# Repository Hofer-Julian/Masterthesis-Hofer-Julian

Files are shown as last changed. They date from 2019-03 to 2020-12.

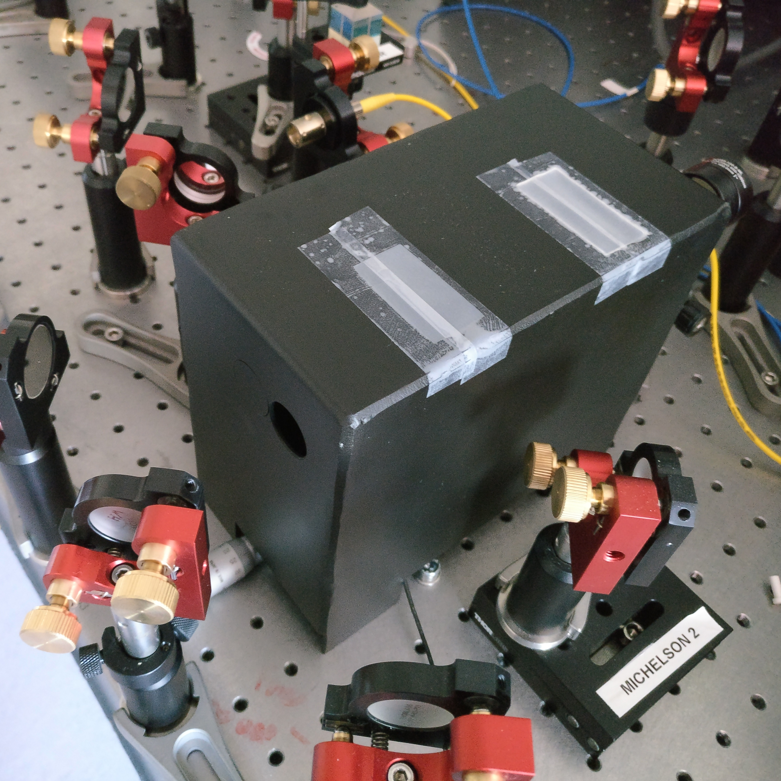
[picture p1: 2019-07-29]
figures/fabry-perot/setup/casing.jpg

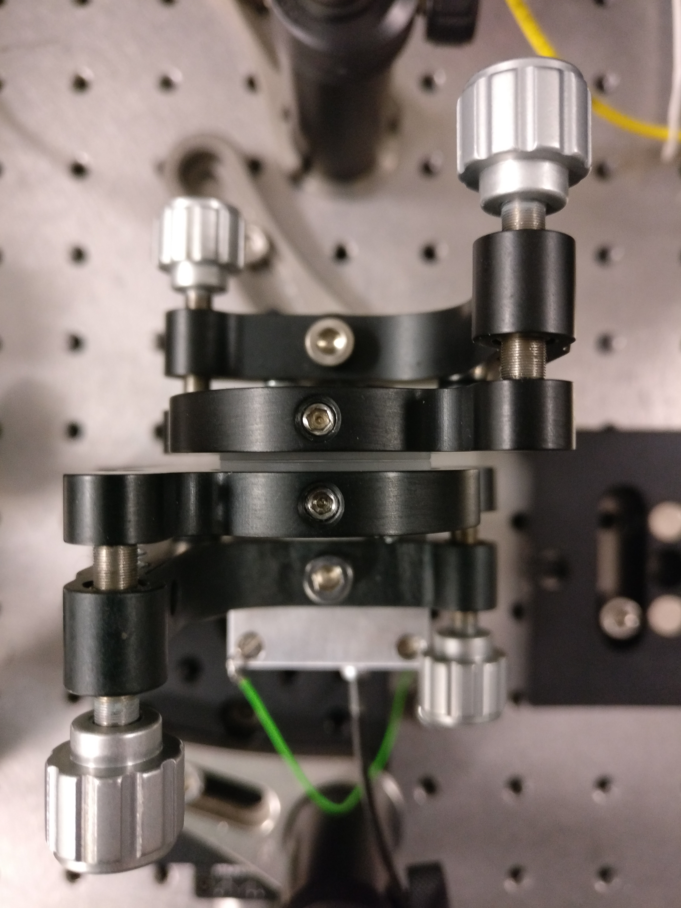
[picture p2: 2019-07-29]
figures/fabry-perot/setup/processing/topview.jpg

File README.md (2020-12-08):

# Advanced excitation and spectroscopy schemes of single quantum dots 

In this thesis excitation of quantum dots via adiabatic rapid passage and spectroscopy of quantum dot emission with a scanning Fabry Pérot interferometer (FPI) are discussed.

First, the use of GaAs quantum dots as sources of (entangled) single photons is motivated and details of their fabrication and optical properties are presented.
The optical setup used for the measurements is sketched and methods like micro photo-luminescence are explained.
Subsequently, the use of adiabatic rapid passage for entangled photon generation is motivated and its implementation with frequency-chirped pulses is explained.

The theory behind the chirp is presented, leading to the description of a setup used to deterministically adjust the chirp of a laser beam.
The chirped beam was measured with an interferometric autocorrelator and the numerical filter MOSAIC was used to extract the chirp parameter from these measurements.

Also, scanning FPIs as tools to resolve fine features of quantum dot emission are presented.
The reader is guided through the theory of Gaussian beams and the calculation of common FPI properties, ranging from resonator losses to its transmission spectrum.
Methods to suppress higher Gauss modes are presented and simulations are shown used to size the FPI.
Finally, measurements with fast photodiodes and CCD sensors are presented and with them the suitability for resolving the fine structure of a GaAs quantum dot is shown.   

------------------
<sub>Masterthesis, 10/2019, Johannes Kepler University, Linz/Austria<sub>

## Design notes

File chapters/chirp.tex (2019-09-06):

% !TEX root = ../masterthesis.tex
\chapter{Entangled photon generation using adiabatic rapid passage with frequency-chirped pulses}
\label{cha:chirp}

\section{Introduction and motivation}

In order to efficiently use the biexciton decay cascade, the \acl{XX} state has to be prepared beforehand in a robust way.
This chapter deals with the efficient inversion of the \ac{QD} from the ground state to the biexciton level via \ac{ARP}.
\acs{ARP} uses chirped pulses, which need to be measured and deterministically adjusted in order to effectively use them.
Therefore, the majority of this chapter will focus on the chirp and how to determine and adjust it, with the help of simulations and later with measurements.

\section{Chirp}
\label{sec:chirp}
A chirped signal is a signal whose frequency changes over time.
For example, the frequency of a linearly chirped signal $f(t)$ would be described by
\begin{equation}
f(t) = ct+f_0
\end{equation}
where $f_0$ is the starting frequency at $t=0$ and $c$ is the chirpyness. A linearly chirped sinusoidal wave is depicted in figure~\ref{fig:chirped-sin}.

\begin{figure}[H]
	\centering
	
	\caption{A chirped sinusoidal wave which increases in frequency over time.}
	\label{fig:chirped-sin}
\end{figure}

As this chapter is concentrated on exciting \acp{QD} with frequency-chirped pulses, the mathematical description of chirped laser pulses will now be discussed. The shape of the electric field of a laser $E(t)$ can be approximated by
\begin{equation}
\label{eq:electric-field-laser}
E(t) \sim \mathrm{Re}\left(f^{1/2}(t) \cdot \exp\left(-i \omega t - i \phi(t)\right)\right)
\end{equation}
with the central frequency $\omega$ and the linear chirp $\phi(t)$.

Depending on the laser either a Gaussian or a hyperbolic secant describes the pulse shape more accurately~\cite{glassl_biexciton_2013, hirayama_real-time_2002}

\begin{itemize}
	\item Gaussian pulse:
	\begin{itemize}
		\item Pulse shape of
		\begin{equation}
		\label{eq:f_gauss}
		f_{gauss}(t) = \left(\frac{A_{gauss}}{\sqrt{2 \cdot \pi \cdot \tau_0 \cdot \tau}} \exp\left(-\frac{t^2}{2 \cdot \tau^2}\right)\right)^2
		\end{equation}
		with the normalization constant $A_{gauss}$, the pulse duration $\tau_0$, the central frequency $\omega$ and the chirp coefficient $\alpha$.
		\item Linear chirp of
		\begin{equation}
		\label{eq:phi-gauss}
		\phi_{gauss}(t) = \frac{a_{gauss} t^2}{2}
		\end{equation}
		where 
		\begin{equation}
		\tau = \sqrt{\alpha^2 / \tau_0^2 + \tau_0^2}
		\end{equation}
		characterizes the chirped pulse length and
		\begin{equation}
		\label{eq:chirp-parameter}
		a = \alpha / (\alpha ^ 2 + \tau _0 ^ 4)
		\end{equation}
		is the frequency chirp rate.
	\end{itemize}
	\newpage
	\item Secant pulse:
	\begin{itemize}
		\item Pulse shape of
		\begin{equation}
		f_{secant}(t) = A_{secant} \cdot \textrm{sech}^2\left(\frac{t}{\tau_0}\right) = A_{secant} \cdot \left(\frac{2}{\exp(\frac{t}{\tau_0}) + \exp(-\frac{t}{\tau_0})}\right)^2
		\end{equation}
		with the normalization constant $A_{secant}$, the pulse duration $\tau_0$, the central frequency $\omega$ and the chirp coefficient $\alpha$.
		\item Linear chirp of
		\begin{equation}
		\phi_{secant}(t) = \alpha_{secant}\left(\frac{t}{\tau_0}\right)^2
		\end{equation}
	\end{itemize}
\end{itemize}

The following discussion will assume a Gaussian laser shape as described by equation~\eqref{eq:f_gauss} and \eqref{eq:phi-gauss}.
A simulation for $E$ is plotted in figure~\ref{fig:chirpedlaserpulse} for different chirp parameters $\alpha$ suitable to display examples for strong and weak chirps.
As can be seen there, the chirp parameter strongly influences the shape of the electric field.
If $E$ could be measured directly, the chirp could be easily estimated.
This is not feasible in our case, as our Ti:Sa laser can produce laser pulses as short as \SI{100}{\femto \second} and response times of photodiodes and oscilloscopes are in the best case in the order of \SI{200}{\femto \second}.
This means they cannot even measure the duration of these ultrashort pulses let alone resolve the pulse shape.

\begin{figure}[H]
	\centering
	
	\caption{Electric field $E$ of Gaussian laser pulse of pulse duration $\tau_0=\SI{0.5}{\pico \second}$ for chirp of (a) $\alpha = \SI{0.1}{\pico \second \squared}$ and (b) $\alpha = \SI{0.5}{\pico \second \squared}$}
	\label{fig:chirpedlaserpulse}
\end{figure}

\newpage

\section{Measuring the chirp with interferometric autocorrelation}
\begin{figure}[H]
	\centering
	
	\caption[Schematics of an interferometric autocorrelator]{Schematics of an interferometric autocorrelator, where \textbf{L} is a converging lens, \textbf{SHG} a second-harmonic generation crystal, \textbf{BS} a beam splitter, \bm{$\tau$} the interval between two pulses, \textbf{D} the detector and \textbf{F} a spectral filter to block the fundamental wavelength~\cite{noauthor_optical_nodate}.}
	\label{fig:optical-field-autocorrelation-setup}
\end{figure}
In order to estimate the pulse width $\tau_0$, \ac{IAC} is used.
Basically, a nonlinear crystal is added to a Michelson interferometer in order to generate a signal governed by
\begin{equation}
\label{eq:i-m-integral}
I_M(\tau) = \int_{-\infty}^{+\infty}\langle|(E(t)+E(t-\tau))^2|^2\rangle dt.
\end{equation}
and plotted in figure~\ref{fig:imgausschirpwithoutslitwithoutmosaic}~\cite{diels_ultrashort_2006}.
Here, $\langle \rangle$ denotes averaging over fast oscillations of the electric field.
\begin{figure}[H]
	\centering
	
	\caption{Intensity of IAC of a Gaussian laser pulse of pulse duration $\tau_0=\SI{0.5}{\pico \second}$ without applied MOSAIC filter for chirp of (a) $\alpha = \SI{0.1}{\pico \second \squared}$ and (b) $\alpha = \SI{0.5}{\pico \second \squared}$}
	\label{fig:imgausschirpwithoutslitwithoutmosaic}
\end{figure}
Under the use of equation~\ref{eq:electric-field-laser}, equation~\eqref{eq:i-m-integral} can be expanded to
\begin{align}
I(\tau) = 1 &+ 2 \int f(t) f(t + \tau) dt + \int f(t) f(t + \tau) \cos(2 \omega \tau + 2 \Delta \phi) dt \nonumber\\
&+ 2 \int f^{1/2}(t) f^{3/2}(t + \tau) \cos(\omega \tau + \Delta \phi) dt + 2 \int f^{3/2}(t) f^{2/2}(t + \tau) \cos(\omega \tau + \Delta \phi) dt
\end{align}
where $\Delta \phi(t, \tau) = \phi(t + \tau) - \phi(t)$ and $\int f(t) dt = 1$.

As can be seen in figure~\ref{fig:imgausschirpwithoutslitwithoutmosaic}, the chirp parameter $\alpha$ has hardly any measurable influence on the resulting signal.
However, certain modifications to the \ac{IAC} signal introduced by \textcite{hirayama_real-time_2002} make it much more sensitive to the temporal chirp.
It is called \ac{MOSAIC} and performs the following transformations on the \ac{IAC} spectrum: The $\omega$ terms are eliminated and the $2\omega$ term is doubled.
The \ac{MOSAIC} signal is then described by
\begin{equation}
\label{eq:i-m-filtered}
I_{M}(\tau) = 1 + 2 \int f(t) f(t + \tau) dt + 2 \int f(t) f(t + \tau) \cos(2\omega \tau + 2\Delta \phi) dt.
\end{equation}
When the MOSAIC filter is applied to the data in figure~\ref{fig:imgausschirpwithoutslitwithoutmosaic}, this results in a signal as shown in figure~\ref{fig:mosaicchirpedlaserpulse}.
Here the influence of the chirp is clearly visible in the lower envelope.
\begin{figure}[H]
	\centering
	
	\caption{Intensity of IAC of a Gaussian laser pulse of pulse duration $\tau_0=\SI{0.5}{\pico \second}$ for chirp of (a) $\alpha = \SI{0.1}{\pico \second \squared}$ and (b) $\alpha = \SI{0.5}{\pico \second \squared}$}
	\label{fig:mosaicchirpedlaserpulse}
\end{figure}

\newpage

The points of the lower envelope can be obtained by determining the local minima of the signal as shown in figure~\ref{fig:mosaicchirpedlaserpulsefindenvelope}.

\begin{figure}[H]
	\centering
	
	\caption{Intensity of IAC of a Gaussian laser pulse of pulse duration $\tau_0=\SI{0.5}{\pico \second}$ with applied MOSAIC filter for chirp of (a) $\alpha = \SI{0.1}{\pico \second \squared}$ and (b) $\alpha = \SI{0.5}{\pico \second \squared}$.
		The orange dots are results of a numerical peak finder algorithm, executed in order to find local minima.}
	\label{fig:mosaicchirpedlaserpulsefindenvelope}
\end{figure}

The lower bound (minima envelope) of the MOSAIC trace can be derived by use of a standard textbook procedure~\cite{klein_optics_1986}
\begin{equation}
S^{min}_{MOSAIC}(\tau)= 1 + 2 \cdot g(\tau) - 2 \cdot [g_s^2(\tau)+g_c^2(\tau)]^{1/2}
\end{equation}
with
\begin{align}
g(\tau)&=\int f(t)f(t+\tau)dt\\
g_s(\tau)&=\int f(t)f(t+\tau)\sin(2\Delta\phi)dt\\
g_c(\tau)&=\int f(t)f(t+\tau)\cos(2\Delta\phi)dt.
\end{align}
The points of the lower envelope determined before can now be fitted in order to obtain the chirp parameter $\alpha$ as shown in figure~\ref{fig:mosaicchirpedlaserpulsefitenvelope}.
It is visible that the fitted values of $\alpha$ correspond to the expected values.
\begin{figure}[H]
	\centering
	
	\caption[Intensity of IAC of a Gaussian laser pulse of pulse duration $\tau_0=\SI{0.5}{\pico \second}$ with applied MOSAIC filter and fitted $\alpha$-values.]{Intensity of IAC of a Gaussian laser pulse of pulse duration $\tau_0=\SI{0.5}{\pico \second}$ with applied MOSAIC filter for chirp of (a) $\alpha = \SI{0.1}{\pico \second \squared}$ and (b) $\alpha = \SI{0.5}{\pico \second \squared}$.
		The orange line is a fit for the lower envelope of the MOSAIC signal in order to obtain~$\alpha$.}
	\label{fig:mosaicchirpedlaserpulsefitenvelope}
\end{figure}

\section{Deterministically adjusting the chirp with a pulse expander}
\label{sec:pulse-expander}
\begin{figure}[H]
	\centering
	
	\caption[Scheme of a folded pulse expander as described by \textcite{martinez_3000_1987}.]{Scheme of a folded pulse expander as described by \textcite{martinez_3000_1987}.
		The light enters on the right side, passes the halfmirror, and enters the system of transmission grating, lens and mirrors.
		Afterwards it hits the halfmirror and exits on the left hand.
		It induces an accumulated group velocity dispersion on the signal depending on the optical distance between the transmission grating and the lens.}
	\label{fig:pulse-expander}
\end{figure}

In the optimal case the chirp of the pulse can be deterministically adjusted in order to most efficiently excite the \ac{QD} via adiabatic rapid passage (going to be introduced in section~\ref{sec:arp}).
Grating compressors as discussed by \textcite{martinez_3000_1987} were originally used to compensate the broadening effect fibers have on pulses.
However, together with a telescope they have the inverse effect and can be used to induce a chirp.
A setup like this is sketched in figure~\ref{fig:pulse-expander} and it will in future references in this work be called \textit{pulse expander}.
Its main elements are a transmission grating and a lens.
This folded setup uses a mirror after the lens so that only one lens and one mirror are needed.
The accumulated group velocity dispersion $\frac{d^2 \Phi}{d \omega^2}$ can be adjusted by varying the optical distance $d$ between the focal plane of the lens and the transmission grating and is described by
\begin{equation}
\frac{d^2 \Phi}{d \omega^2} = k \beta^2 2 d
\end{equation}
where $k$ is the wavenumber and $\beta$ is given by
\begin{equation}
\beta = \frac{\lambda}{2 \pi w_0 \cos \theta}
\end{equation}
with $\lambda$ denoting the centre wavelength, $w_0$ the beam waist (beam size at the point of its focus) and $\theta$ the emerging angle as sketched in figure~\ref{fig:pulse-expander}.

\begin{figure}[H]
	\centering
	
	\caption{Influence of group velocity dispersion for example inside a fiber on a Gaussian pulse~\cite{orfanidis_electromagnetic_2002}}
	\label{fig:group-velocity-dispersion}
\end{figure}

As can be seen in figure~\ref{fig:group-velocity-dispersion}, a group velocity dispersion has a similar effect on a Gaussian pulse as a chirp.
In fact, the frequency chirp rate $a_{gauss}$ introduced in equation~\eqref{eq:phi-gauss} can be put into relation with it by:~\cite{orfanidis_electromagnetic_2002}
\begin{equation}
a_{gauss} = \frac{\frac{d^2 \Phi}{d \omega^2}}{\tau_0^4 + \left(\frac{d^2 \Phi}{d \omega^2}\right)^2}
\end{equation}

\section{Adiabatic rapid passage}
\label{sec:arp}
One way to invert the \ac{QD} from the ground state $\ket{G}$ to the biexciton state $\ket{XX}$ is by exciting it with a narrow-band laser pulse of constant centre frequency, which equals to half of the ground state biexciton transition frequency.
As described in equation~\eqref{eq:n-xx}, if the pulse area $\theta=\pi$, a population inversion from the $\ket{G}$ state to the $\ket{XX}$ occurs.
However, the $\pi$-pulse method is not a generally robust scheme.
In order to ensure the inversion, precise control of the field intensity is required~\cite{glassl_biexciton_2013}.
Adiabatic rapid passage \acused{ARP} (\acs{ARP}) with frequency chirped pulses is a much more robust alternative to this Rabi-flopping scheme.
Here, the frequency of the laser signal is swept through resonance, starting slightly above or below the resonance frequency.
The biexciton state can be populated with nearly perfect efficiency~\cite{glassl_biexciton_2013} if the process is performed adiabatically, i.e. if~\cite{malinovsky_general_2001}
\begin{equation}
\Omega_0^2 \gg |\frac{d}{dt} \omega(t)|
\end{equation}
where $\Omega_0$ is the peak Rabi frequency and $\omega(t)$ is the center frequency of the laser pulse. 

In figure~\ref{fig:biexciton-occupation} simulations in order to determine the final biexciton occupation for different biexciton binding energies $\Delta$ by \textcite{glassl_biexciton_2013} are presented.
Here, a linearly-chirped Gaussian laser pulse as discussed in section~\ref{sec:chirp} was assumed.
\begin{figure}[H]
	\centering
	
	\caption[Final biexciton occupation after chirped Gaussian pulse of pulse duration $\tau_0 = \SI{2}{\pico \second}$]{Final biexciton occupation after chirped Gaussian pulse of pulse duration $\tau_0 = \SI{2}{\pico \second}$.
		It is plotted against the original pulse area $A$ (vertical axis) and the chirp parameter $\alpha$ for biexciton binding energies of (a) $\Delta=0$, (b) 1, and (c) \SI{3}{\milli \electronvolt}~\cite{glassl_biexciton_2013}.}
	\label{fig:biexciton-occupation}
\end{figure}
The central frequency is chosen so that for $\alpha=0$ it resonates to groundstate-to-biexction transition, which is sketched in figure~\ref{fig:biexciton-occupation}.
For $\alpha=0$ Rabi oscillations are visible and their period depends strongly on the biexciton binding energy $\Delta$.
However, for $\alpha \gg 0$ biexciton preparation becomes insensitive to small variations of the pulse area $A$ as long it exceeds a certain threshold.
This is therefore the regime which would be the most suitable to work in.
In the case of $\alpha < 0$ this insensitivity does not appear for moderate values of $\Delta$ as can be seen in figure~\ref{fig:biexciton-occupation}(b).

\newpage
\section{Measurements and discussion}
As discussed in the sections above, the final goal is to excite a \ac{QD} via \ac{ARP}.
The first step to do that is to determine the chirp of a laser pulse which only passed the pulse shaper with the \ac{IAC}.
Here a laser pulse of only $\tau_0=\SI{344}{\femto \second}$ was used as the \ac{IAC} can not resolve fine enough details for greater $\tau_0$.
Even though broader peaks will be necessary in order to excite the \ac{QD} with \ac{ARP}, this is not a problem as the equivalent chirp can be calculated for greater $\tau_0$ with equation~\eqref{eq:chirp-parameter}.

Afterwards, a signal was measured after passing a pulse expander as discussed in section~\ref{sec:pulse-expander} and sketched in figure~\ref{fig:setupflat}.
The comparison between these two is shown in figure~\ref{fig:measuredchirpedlaserpulsebeforemosaic}.
Compared to the simulations in figure~\ref{fig:imgausschirpwithoutslitwithoutmosaic} it is visible that the \ac{IAC} of the laser pulse without the pulse expander fits the expected shape well, while the one with the pulse expander does not.
Possible reasons could be that the chirp is too high for the model used in the simulation to work or that the pulse expander introduces side effects not considered in the simulation.

\begin{figure}[H]
	\centering
	
	\caption{Measured IAC of Ti:Sa Laser without (a) and with (b) pulse expander before the autocorrelator.}
	\label{fig:measuredchirpedlaserpulsebeforemosaic}
\end{figure}

The same signals after applying the \ac{MOSAIC} filter are shown in figure~\ref{fig:measuredchirpedlaserpulseaftermosaic}.
It is visible that the lower envelopes in figure~\ref{fig:measuredchirpedlaserpulseaftermosaic}a and \ref{fig:measuredchirpedlaserpulseaftermosaic}b do not resemble the expected ones in figure~\ref{fig:mosaicchirpedlaserpulse}.
As the laser signal without pulse expander was assumed to be relatively unchirped, it is already unexpected that the lower envelope differs that much from a constant line at zero intensity.
One explanatory approach could be that the laser was already chirped to begin with. However, this would not explain why the shape of the lower envelope differs from the characteristic one of the simulation.
The next approach was to send the laser without pulse shaper into the \ac{IAC}.
However, the envelope of the signal after applying the \ac{MOSAIC} filter showed no visible difference to the signal which has not passed a pulse shaper (depicted in figure~\ref{fig:measuredchirpedlaserpulseaftermosaic}).

\begin{figure}[H]
	\centering
	
	\caption{Measured IAC of Ti:Sa Laser with applied MOSAIC filter without (a) and with (b) pulse expander before the autocorrelator.}
	\label{fig:measuredchirpedlaserpulseaftermosaic}
\end{figure}

The next step would have been to deterministically excite the \ac{QD} with \ac{ARP}.
However, it might be advisable to repeat the same procedure with another ultrashort pulsed laser before in order to rule out that our laser is already heavily chirped to begin with.
Alternatively, \ac{ARP} with the pulse expander can be attempted without measuring the chirp first and iteratively adjusting the lens-grating distance until the optimum is reached.

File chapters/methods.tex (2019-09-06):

% !TEX root = ../masterthesis.tex
\chapter{Methods}
\label{cha:methods}

\section{Optical setup}

\begin{figure}[H]
	\centering
	
	\caption[Complete experimental setup]{Complete experimental setup, which was used in order to quantify the chirp of the Ti:Sa Laser and resolve spectral emission of a quantum dot~\cite{schimpf_towards_2017}.}
	\label{fig:setupflat}
\end{figure}

The setup used for the measurements described in following chapters is sketched in figure~\ref{fig:setupflat}.
This setup involves a Ti:Sa laser producing pulses which are sent through a pulse shaper.
Its chirp can be modified with the pulse expander and measured with the interferometric autocorrelator as will be discussed in chapter~\ref{cha:chirp}.
The CW diode laser is used in order to find a suitable \ac{QD} via photoluminescence spectroscopy and the white light enhances the brightness of some \acp{QD} by reducing blinking~\cite{jahn_artificial_2015}.
The spectrometer is then used to measure \ac{QD} emission either with a CCD or an APD.  

\section{Pulse shaper}

In order to resonantly excite the $\ket{XX}$ state a pulsed Ti:Sa laser with a \ac{FWHM} pulse duration of $\tau_P\approx\SI{100}{\femto \second}$ is used.
Under the assumption that the laser pulse is of Gaussian shape and that it is chirp-free (more on that in chapter~\ref{cha:chirp}), the spectral bandwidth $\Delta \nu$ can be described by~\cite{sipek_spectral_2016}
\begin{equation}
\Delta \nu \tau_P \approx 0.44.
\end{equation}
This corresponds to a spectral range of $\Delta E = h\Delta \nu = \SI{18.2}{\milli \electronvolt}$.
As can be seen in equation~\eqref{eq:e_p}, the spectral range should be smaller than $E_B/2\approx\SI{1.89}{\milli \electronvolt}$, which is not fulfilled with the laser beam alone.

The pulse shaper sketched in the upper part of figure~\ref{fig:setupflat} is used in order to tune $\Delta E$ and additionally the centre emission energy to our requirements.
The laser beam is sent through a Keplerian telescope in order to expand its beam diameter from \SI{3.4}{\milli \meter} to \SI{6}{\milli \meter}.
The beam gets dispersed by a diffraction grating and then focused by a lens so that the spectral components are ordered along the Fourier plane where a slit is placed.
The centre energy can be adjusted with the slit position and the spectral range with the slit width.
The setup is mirrored with an additional lens and diffraction grating, which transform the laser beam back into real space. 

\section{Micro photo-luminescence}

The following chapters will investigate the optical properties of \acp{QD}.
In order to achieve that, it is necessary to excite and collect light of only a single \ac{QD}.
This is achieved by \ac{MPL}, which involves (i) reducing the diameter of the excitation laser beam and (ii) using samples with a low \ac{QD} density~\cite{reindl_characterisation_2014}.
(i) can be improved by using an objective, where its minimal achievable spot size $d$ is described by the Abbe limit
\begin{equation}
d = \frac{\lambda}{2 \cdot NA}
\end{equation}
with $NA$ as the numerical aperture.
As the wavelength of the laser $\lambda$ is adjusted according to the optical properties of the \ac{QD}, $NA$ is the adjustable factor.
In our laboratory, objectives between $NA=0.42$ and $NA=0.85$ are used, allowing laser spot sizes in the order of the excitation wavelength.
A \ac{QD} density of approximately $1 / \lambda^2$ is therefore necessary in order to examine the emission of a single \ac{QD}.

\begin{figure}[H]
	\centering
	
	\caption{Laser beam of different spot sizes illuminating quantum dots~\cite{reindl_characterisation_2014}.}
	\label{fig:micro-pl}
\end{figure}

The sample containing the \acp{QD} is mounted inside a cryostat, which is cooled down to \SI{4}{\kelvin}.
This is necessary to limit spectral broadening due to phonons.
The laser beam is focused on the sample by the objective and the \ac{QD} emission is then collected by the very same objective and passed through a beam splitter.

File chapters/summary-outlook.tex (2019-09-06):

% !TEX root = ../masterthesis.tex
\chapter{Summary and outlook}
\label{cha:summary}
This thesis describes the efforts to improve excitation of quantum dots (\ac{QD}s) and to build up a scanning \acl{FPI} which allows to resolve fine details of \ac{QD} emission spectra.
In order to excite the \ac{QD} via adiabatic rapid passage the chirp of the exciting laser beam needs to be deterministically adjustable.
This again requires to build up a setup suitable to manipulate the chirp and a way to determine the chirp parameter $\alpha$.
The laser beam is measured with an interferometric auto correlator.
However, the shape of this measurement depends only weakly on $\alpha$.
Therefore, the numerical filter \ac{MOSAIC} is applied, which resulted in a signal of which the lower envelope depends strongly on $\alpha$.
The simulations show that a fit of the lower envelope of the \ac{MOSAIC} signal allows to determine the chirp parameter.
A pulse expander was built up, with the goal of deterministically adjusting the chirp by adapting the distance between two optical elements.
Measurements with a Ti:Sa laser with and without a pulse expander were conducted, which suggested that the laser signal without the pulse expander is already heavily chirped.
That is why future experiments will investigate different laser models and then compare the measurements with the chirped signal after the pulse expander.
Additionally, the laser emission shape will be described more accurately in future simulations with a frequency comp instead of a simple Gaussian in order to better understand the influence of this approximation.
Afterwards, \acp{QD} will be excited via adiabatic rapid passage.
This topic was not continued, because the Ti:Sa laser had to undergo maintenance for several months which blocked further investigations.

The second topic of this thesis is the build-up of a scanning \ac{FPI}.
Simulations show that common optical components are sufficient to build up an \ac{FPI} which is able to resolve the zero-phonon line of the \ac{QD} emission.
Measurements with planar mirrors show the instability of this arrangement, which is why we switched to planar-concave mirrors.
The \ac{FPI} is aligned with a HeNe laser and fast photodiodes, allowing to adjust the optical components of the \ac{FPI} with direct feedback.
Together with mode matching and spatial filtering, this allows to resolve the fine structure splitting of the excitonic energy levels of the \ac{QD}.
The transmission is determined to be \SI{5}{\percent} and the thermal shift of the \ac{FPI} modes is estimated to be $\approx \SI{66}{\percent}$ of one free spectral range per Kelvin.
Both the transmission and the thermal drift are sufficient for resolving the splitted excitonic emission line. However, the measured finesse of $45$ is too low to resolve near-Fourier-limited zero-phonon-lines.
Also mode-matching and spatial-filtering is time consuming and error prone, which makes them impractical for common measurements.
Therefore, the \ac{FPI} is going to be used with mirrors of higher reflectivity and lower curvature radius and order to gain higher finesse and to use the \ac{FPI} in the confocal mode.
Here, the curvature radius is equal to the mirror distance, which removes the flexibility to change resolution and free spectral range of the \ac{FPI}.
However, the cavity becomes mode-degenerated and therefore liberates from mode matching considerations.
The needed mirrors are already designed and ordered, however it was not possible to test the operation within the duration of this thesis.

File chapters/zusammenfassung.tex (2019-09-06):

% !TEX root = ../masterthesis.tex
% !TEX spellcheck = de-DE

\chapter*{Zusammenfassung}
\label{cha:zusammenfassung}

In dieser Arbeit wird die Anregung von Quantenpunkten mittels Adiabatic Rapid Passage und die Spektroskopie der Quantenpunktemission mit einem Scanning Fabry Pérot Interferometer (FPI) diskutiert.
Zunächst wird die Verwendung von GaAs-Quantenpunkten als Quelle für Einzelphotonen und verschränkten Photonenpaare motiviert und Details zu deren Herstellung und optischen Eigenschaften vorgestellt.
Der für die Messungen verwendete optische Aufbau wird skizziert und es werden Methoden wie die Mikro-Photolumineszenz erläutert.
Anschließend wird die Verwendung von Adiabatic Rapid Passage zur Erzeugung verschränkter Photonen motiviert und deren Implementierung mit frequenz-gechirpten Pulsen erläutert.
Die Theorie hinter dem Chirp wird vorgestellt und führt zur Beschreibung einer Anordnung, mit der der Chirp eines Laserstrahls deterministisch eingestellt werden kann.
Der gechirpte Strahl wurde mit einem interferometrischen Autokorrelator gemessen und der numerische Filter MOSAIC wurde verwendet, um den Chirp-Parameter aus diesen Messungen zu extrahieren.

Schließlich werden Scanning FPIs als Werkzeuge zum Auflösen feiner Merkmale der Quantenpunktemission vorgestellt.
Der Leser / die Leserin wird durch die Theorie der Gaußschen Strahlen und die Berechnung allgemeiner FPI-Eigenschaften geführt, die von Resonatorverlusten bis zu ihren Transmissionsspektrum reichen.
Es werden Methoden zur Unterdrückung höherer Gauß-Modi vorgestellt und Simulationen zur Größenbestimmung der Bauteile des FPIs gezeigt.
Abschließend werden Messungen mit schnellen Fotodioden und CCD-Sensoren vorgestellt und damit die Eignung zum Auflösen der Feinstruktur eines GaAs-Quantenpunktes gezeigt.

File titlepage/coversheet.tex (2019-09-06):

%%Andreas Neubauer, May 2016
\documentclass[12pt,a4paper]{article}
\usepackage{graphicx}
\usepackage{xcolor}
\textwidth 16.7cm
\textheight 25cm
\topmargin -2.7cm
\oddsidemargin 0.25cm
\parindent 0pt
\pagestyle{empty}
\begin{document}
%
% -------- only change entries beginning here ----------------------------
%
% choose language of coverpage: german or english
\newif\ifeng
\engtrue
%\engfalse
%
%
% enter the title of the thesis
%
\def\title{Advanced excitation and spectroscopy schemes of single quantum dots}
%
%
% choose type of work: 0 ... Dissertation
%                      1 ... Diplomarbeit
%                      2 ... Masterarbeit
\def\type{2}
%
%
% enter name of degree, see examples below (as stated in your curriculum)
%
% e.g. Masterstudium
\def\degree{Diplom-Ingenieur}
%\def\degree{Diplom-Ingenieurin}
%\def\degree{Master of Science}
%
% e.g. Diplomstudium Lehramt
%\def\degree{Magister der Naturwissenschaften}
%\def\degree{Magistra der Naturwissenschaften}
%
% e.g. Doktorratsstudium
%\def\degree{Doktor der technischen Wissenschaften}
%\def\degree{Doktorin der technischen Wissenschaften}
%\def\degree{Doktor der Naturwissenschaften}
%\def\degree{Doktorin der Naturwissenschaften}
%
%
% enter the study (Studienrichtung, as stated in your curriculum)
%
% e.g. Diplomstudium:
%\def\study{Lehramt Mathematik}
%
% e.g. Masterstudium:
\def\study{Technische Physik}
%
% e.g. Doktorratsstudium
%\def\study{Technische Wissenschaften}
%\def\study{Naturwissenschaften}
%
%
% If the names for the following entries are too long, break them into several
% lines using \\
%
%
% enter the name of the student
%
\def\name{Julian Hofer, B.Sc.}
%
%
% enter the name of the institute (use translation for english version)
% e.g.
%\def\institute{Industrial Mathematics\\ Institute}
%\def\institute{Institut f\"ur\\ Industriemathematik}
%
\def\institute{Institute of Semiconductor and Solid State Physics}
%
%
% enter the name of the supervisor and first thesis examiner
% only for type 0 (Dissertation) you need a second thesis examiner
%
% for the german version you also have to enter the sex (male or female)
% of the supervisor/examiners
%
\def\supervisor{Prof. Dr. Armando Rastelli}
\newif\ifsupvismale
\supvismaletrue
%\supvismalefalse
%
\def\secondexaminer{Name of 2. examiner}
\newif\ifsecexmale
\secexmaletrue
%\secexmalefalse
%
%
% if there has been assistance by a further person uncomment the following line
% and enter the name.
%
\def\assist{DI Christian Schimpf}
%
%
% enter month year
% (the month when you brought it to the Prüfungs- und Anerkennungsservice)
%
\def\date{September 2019}
%
% do not change anything below this line
% -------------------------------------------------------------------------------
%
\def\ifundefined#1{\expandafter\ifx\csname#1\endcsname\relax}
\DeclareFontShape{OT1}{cmss}{m}{n}
  {<5><6><7><8><9><10><10.95><12><14.4><17.28><20.74><24.88><29.86><35.83>%
   <42.99><51.59><67><77.38>cmss10}{}
\DeclareFontShape{OT1}{cmss}{bx}{n}
  {<5><6><7><8><9><10><10.95><12><14.4><17.28><20.74><24.88><29.86><35.83>%
   <42.99><51.59><67><77.38>cmssbx10}{}
\makeatletter
\def\Huge{\@setfontsize\Huge{29.86pt}{36}}
\makeatother
%
\unitlength 1cm
\sffamily
\begin{picture}(16.7,0)
\ifeng
 \put(11.5,-2.5){}
\else
 \put(11.5,-2.5){}
\fi
\put(12.9,-4.2){\begin{minipage}[t]{3.9cm}\footnotesize%
\ifeng
 Submitted by\\
\else
 Eingereicht von\\
\fi
{\bfseries\name}%
\vskip 4mm%
\ifeng
 Submitted at\\
\else
 Angefertigt am\\
\fi
{\bfseries\institute}%
\vskip 4mm%
\ifcase\type%
 \ifeng
  Supervisor and\\ First Examiner\\
 \else
  \ifsupvismale%
   Betreuer und\\ Erstbeurteiler\\
  \else
   Betreuerin und\\ Erstbeurteilerin\\
  \fi
 \fi
 {\bfseries\supervisor}%
 \vskip 4mm%
 \ifeng
  Second Examiner\\
 \else
  \ifsecexmale%
   Zweitbeurteiler\\
  \else
   Zweitbeurteilerin\\
  \fi
 \fi
 {\bfseries\secondexaminer}%
\else
 \ifeng
  Supervisor\\
 \else
  \ifsupvismale%
   Betreuer\\
  \else
   Betreuerin\\
  \fi
 \fi
 {\bfseries\supervisor}%
\fi
\vskip 4mm%
\ifundefined{assist}\else
 \ifeng
  Co-Supervisor\\
 \else
  Mitbetreuung\\
 \fi
 {\bfseries\assist}%
\vskip 4mm%
\fi
\date
\end{minipage}}
\put(12.9,-25){\begin{minipage}[t]{3.9cm}\footnotesize%
{\bfseries JOHANNES KEPLER\\
\ifeng
 UNIVERSITY
\else
 UNIVERSIT\"AT
\fi
LINZ}\\
Altenbergerstra{\ss}e 69\\
4040 Linz, \"Osterreich\\
www.jku.at\\
DVR 0093696
\end{minipage}}
\put(0,-12.2){\begin{minipage}[b]{12cm}\Huge\bfseries\title\end{minipage}}
\put(0,-17.2){}
\put(0,-18.3){\begin{minipage}[t]{12cm}%
\ifeng
 {\large\ifcase\type Doctoral \or Diploma \or Master \fi Thesis}%
 \vskip 2mm%
 to obtain the academic degree of%
 \vskip 3mm%
 {\large\degree}
 \vskip 3mm%
 in the \ifcase\type Doctoral \or Diploma \or Master's \fi Program
\else
 {\large\ifcase\type Dissertation\or Diplomarbeit\or Masterarbeit\fi}%
 \vskip 2mm%
 zur Erlangung des akademischen Grades%
 \vskip 3mm%
 {\large\degree}
 \vskip 3mm%
 im \ifcase\type Doktoratsstudium \or Diplomstudium\or Masterstudium\fi
\fi
\vskip 3mm%
{\large\study}
\end{minipage}}
\end{picture}
\end{document}

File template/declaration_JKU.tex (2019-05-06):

%%%% Time-stamp: <2017-02-14 16:01:12 vk>
%% ========================================================================
%%%% Disclaimer
%% ========================================================================
%%
%% created by
%%
%%      Karl Voit, and Matthias Wölbitsch
%%
%%
%% code for the date and signature fields adapted from
%% http://tex.stackexchange.com/a/20562

\newcommand{\textfield}[2]{
  \vbox{
    \hsize=#1\kern3cm\hrule\kern1ex
    \hbox to \hsize{\strut\hfil\footnotesize#2\hfil}
  }
}

\ifthenelse{\boolean{english_affidavit}}{
  \section*{Affidavit}
  I declare that I have authored this thesis independently, that I have
  not used other than the declared sources/resources, and that I have
  explicitly indicated all material which has been quoted either
  literally or by content from the sources used. The text document
  uploaded to \myacro{TUGRAZ}online is identical to the present master‘s
  thesis.

  \hbox to \hsize{\textfield{4cm}{Date}\hfil\hfil\textfield{7cm}{Signature}}
}{
  \section*{Eidesstattliche Erklärung}
  \foreignlanguage{ngerman}{%
    Ich erkläre an Eides statt, dass ich die vorliegende Masterarbeit selbstständig und ohne fremde Hilfe verfasst, andere als die angegebenen Quellen und Hilfsmittel nicht benutzt bzw. die wörtlich oder sinngemäß entnommenen Stellen als solche kenntlich gemacht habe.
    Die vorliegende Masterarbeit ist mit dem elektronisch übermittelten Textdokument identisch.}

    \hbox to \hsize{\textfield{4cm}{Datum}\hfil\hfil\textfield{7cm}{Unterschrift}}
}
\newpage

%%% Local Variables:
%%% mode: latex
%%% mode: auto-fill
%%% mode: flyspell
%%% TeX-master: "../main"
%%% End:

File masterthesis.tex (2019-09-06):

% !BIB program = biber

%%%% Time-stamp: <2018-03-24 14:05:09 vk>
%% ========================================================================
%%%% Disclaimer
%% ========================================================================
%%
%% created by
%%
%%      Karl Voit
%%

%% ========================================================================
%%%% Basic settings
%% ========================================================================
%% (idea of using newcommands for basic documentclass settings from: Thomas Schlager)

\newcommand{\mypapersize}{A4}
%% e.g., "A4", "letter", "legal", "executive", ...
%% The size of the paper of the resulting PDF file.

\newcommand{\mylaterality}{twoside}
%% "oneside" or "twoside"
%% Either you are creating a document which is printed on both, left pages
%% and right pages (twoside) or you create a document which is printed
%% on right pages only (oneside).
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
%% template, LaTeX, ...) is added after the title page.
%% Please do not set to "false" without a good reason. The colophon
%% helps your readers to get in touch with LaTeX and to find this template.

\setboolean{myaddlistoftodos}{false}  %% "true" or "false"
%% If set to "true": the current list of open todos is added after the
%% table of contents. If \mytodonotesoptions is set to "disable", no
%% list of todos is added, independent of this setting here.

\setboolean{english_affidavit}{false}  %% "true" or "false"
%% If set to "true": the language of the statutory declaration text is set to
%% English, otherwise it is in German.

%% ========================================================================
%%%% Document metadata
%% ========================================================================

%% general metadata:
\newcommand{\myauthor}{Julian Hofer}  %% also used for PDF metadata (hyperref)
\newcommand{\myauthorwithexistingtitles}{\myauthor{}, BSc}  %% including
                                %% university degree already held
                                %% (BSc, MSc, ...)
\newcommand{\mytitle}{Advanced excitation and spectroscopy schemes of single quantum dots}  %% also used for PDF metadata (hyperref)
\newcommand{\mysubject}{Quantum optics}  %% also used for PDF metadata (hyperref)
\newcommand{\mykeywords}{KEYWORDS}  %% also used for PDF metadata (hyperref)

%% ========================================================================
%%%% MISC command definitions
%% ========================================================================
\input{template/mycommands}

%% ========================================================================
%%%% Typographic settings
%% ========================================================================
\input{template/typographic_settings}

%% ========================================================================
%%%% MISC usepackages
%% ========================================================================

%% ... it's OK to put here your own usepackage commands ...

\usepackage{pdfpages}                   % For including pdf-pages
\usepackage{blindtext}                  % Blindtext
\usepackage{booktabs}                   % Tables
\usepackage{siunitx}                    % Standardized unit usage
\usepackage{float}			          	% Allows strict positioning
\usepackage{amsmath,amssymb,amstext}	% Math
\usepackage{subcaption}                 % Subfigure
\usepackage[printonlyused,withpage]{acronym}
\usepackage{braket}
\usepackage{scalerel,stackengine}       % Equal sign
\usepackage{bm}

%% ========================================================================
%%%% MISC self-defined commands and settings
%% ========================================================================

%% ... it's OK to put here your own newcommand/newenvironment-definitions ...

\sisetup{range-units=brackets}

\newcommand\equalhat{\mathrel{\stackon[1.5pt]{=}{\stretchto{%
				\scalerel*[\widthof{=}]{\wedge}{\rule{1ex}{3ex}}}{0.5ex}}}}

\hyphenation{ex-am-ple hy-phen-ate}  %% in order to use German umlauts
%% here (Ver-\"of-fent-li-chung), you have to check for
%% activated \usepackage[T1]{fontenc} in the preamble

%% override default language of babel: (be sure to know, what you're
%% doing here)
%\selectlanguage{american}
%\selectlanguage{ngerman}

%% ========================================================================
%%%% Templates
%% ========================================================================

%% template for inserting figures:
% \myfig{}%% filename
%       {}%% width/height
%       {}%% caption
%       {}%% optional (short) caption for list of figures
%       {fig:}%% label

%% acronyms in small caps: \myacro{UNESCO}

\input{template/pdf_settings}  %% should be *last* definitions in preamble!
%% ========================================================================
%%%% begin{document}
%% ========================================================================
\begin{document}

\frontmatter                    %% KOMA: roman page numbers and such; only available in scrbook

\input{colophon}                %% defines information about editor, LaTeX, font, ...

%% Choose your desired title page:
\includepdf{\mytitlepage}         %% include title page
\pagenumbering{gobble}            %% Disable page numbering for first few pages
%% Needed for first blank page
\KOMAoptions{open=left}          
\thispagestyle{empty}
\mbox{}
\clearpage

\input{template/declaration_JKU}  %% Statutory Declaration

\input{chapters/acknowledgement}

%% include the abstract without chapter number but include it on table of contents:
\cleardoublepage
\phantomsection
\addcontentsline{toc}{chapter}{Zusammenfassung}
\include{chapters/zusammenfassung}
\addcontentsline{toc}{chapter}{Abstract}
\include{chapters/abstract}              %% Abstract

\tableofcontents                %% this produces the table of contents - you might have guessed :-)

\listoffigures

%% if myaddlistoftodos is set to "true", the current list of open todos is added:
\ifthenelse{\boolean{myaddlistoftodos}}{
  \newpage\listoftodos          %% handy if you are using todonotes with \todo{}
}{}                             %% with todonotes-package option "disable" you can get rid of any todo in the output

\mainmatter                     %% KOMA: marks main part using arabic page numbers and such; only available in scrbook

%% include tex file chapters:
\KOMAoptions{open=right}
\include{chapters/introduction}
\include{chapters/quantum-dot}
\include{chapters/methods}
\include{chapters/chirp}
\include{chapters/fabry-perot}
\include{chapters/summary-outlook}

\appendix                       %% closes main document, appendix follows until end; only available in book-classes
\addpart*{Appendix}             %% adding Appendix to tableofcontents

\chapter{Acronyms}
\begin{acronym}[TDMA]
	\acro{BSM}{Bell state measurement}
	\acro{QD}{quantum dot}
	\acro{FPI}{Fabry Pérot interferometer}
	\acro{FSS}{fine structure splitting}
	\acro{MBE}{molecular beam epitaxy}	
	\acro{CB}{conduction band}
	\acro{VB}{valence band}
	\acro{X}{exciton}
	\acro{XX}{biexciton}
	\acro{ZPL}{zero phonon line}
	\acro{PSB}{phonon side band}
	\acro{FCP}{Franc-Condon principles}
	\acro{APD}{avalanche photodiode}	
	\acro{HBT}{Hanbury-Brown-Twiss}
	\acro{BS}{beam splitter}
	\acro{FWHM}{full width at half maximum}
	\acro{MPL}{micro photo-luminescence}
	\acro{ARP}{adiabatic rapid passage}
	\acro{IAC}{interferometric autocorrelation}
	\acro{MOSAIC}{modified-spectrum autointerferometric correlation}
	\acro{CCD}{charge-coupled device}
	\acro{NIM}{nuclear instrumentation module}
	\acro{BNC}{Bayonet Neill–Concelman}
\end{acronym}

\printbibliography              %% remove, if using BibTeX instead of biblatex
% \include{further_ressources}  %% this is a suggestion: you have to create this file on demand

%%%% end{document}
\end{document}
%% vim:foldmethod=expr
%% vim:fde=getline(v\:lnum)=~'^%%%%\ .\\+'?'>1'\:'='
%%% Local Variables:
%%% mode: latex
%%% mode: auto-fill
%%% mode: flyspell
%%% eval: (ispell-change-dictionary "en_US")
%%% TeX-master: "main"
%%% End:

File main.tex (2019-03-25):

%%%% Time-stamp: <2018-03-24 14:05:09 vk>
%% ========================================================================
%%%% Disclaimer
%% ========================================================================
%%
%% created by
%%
%%      Karl Voit
%%

%% ========================================================================
%%%% Basic settings
%% ========================================================================
%% (idea of using newcommands for basic documentclass settings from: Thomas Schlager)

\newcommand{\mypapersize}{A4}
%% e.g., "A4", "letter", "legal", "executive", ...
%% The size of the paper of the resulting PDF file.

\newcommand{\mylaterality}{twoside}
%% "oneside" or "twoside"
%% Either you are creating a document which is printed on both, left pages
%% and right pages (twoside) or you create a document which is printed
%% on right pages only (oneside).
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
%% "template/title_Thesis_TU_Graz_-_kazemakase":
%%             titlepage for Graz University of Technology
%%             (correct new Corporate Design) by kazemakase (2013):
%%             see https://github.com/novoid/LaTeX-KOMA-template/issues/5
%% "template/title_VWA": titlepage for Vorwissenschaftliche Arbeit

\newcommand{\mytodonotesoptions}{}
%% e.g., "" (empty), "disable", ...
%% Options for the todonotes-package. If "disable", all todonotes will
%% be hidden (including listoftodos).

%% Load main settings for document preamble:
\input{template/preamble}%% DO NOT REMOVE THIS LINE!

\setboolean{myaddcolophon}{true}  %% "true" or "false"
%% If set to "true": a colophon (with notes about this document
%% template, LaTeX, ...) is added after the title page.
%% Please do not set to "false" without a good reason. The colophon
%% helps your readers to get in touch with LaTeX and to find this template.

\setboolean{myaddlistoftodos}{false}  %% "true" or "false"
%% If set to "true": the current list of open todos is added after the
%% table of contents. If \mytodonotesoptions is set to "disable", no
%% list of todos is added, independent of this setting here.

\setboolean{english_affidavit}{false}  %% "true" or "false"
%% If set to "true": the language of the statutory declaration text is set to
%% English, otherwise it is in German.

%% ========================================================================
%%%% Document metadata
%% ========================================================================

%% general metadata:
\newcommand{\myauthor}{Julian Hofer}  %% also used for PDF metadata (hyperref)
\newcommand{\myauthorwithexistingtitles}{\myauthor{}, BSc}  %% including
                                %% university degree already held
                                %% (BSc, MSc, ...)
\newcommand{\mytitle}{TITLE}  %% also used for PDF metadata (hyperref)
\newcommand{\mysubject}{SUBJECT}  %% also used for PDF metadata (hyperref)
\newcommand{\mykeywords}{KEYWORDS}  %% also used for PDF metadata (hyperref)

%% ========================================================================
%%%% MISC command definitions
%% ========================================================================
\input{template/mycommands}

%% ========================================================================
%%%% Typographic settings
%% ========================================================================
\input{template/typographic_settings}

%% ========================================================================
%%%% MISC usepackages
%% ========================================================================

%% ... it's OK to put here your own usepackage commands ...

\usepackage{pdfpages}

%% ========================================================================
%%%% MISC self-defined commands and settings
%% ========================================================================

%% ... it's OK to put here your own newcommand/newenvironment-definitions ...

\hyphenation{ex-am-ple hy-phen-ate}  %% in order to use German umlauts
%% here (Ver-\"of-fent-li-chung), you have to check for
%% activated \usepackage[T1]{fontenc} in the preamble

%% override default language of babel: (be sure to know, what you're
%% doing here)
%\selectlanguage{american}
%\selectlanguage{ngerman}

%% ========================================================================
%%%% Templates
%% ========================================================================

%% template for inserting figures:
% \myfig{}%% filename
%       {}%% width/height
%       {}%% caption
%       {}%% optional (short) caption for list of figures
%       {fig:}%% label

%% acronyms in small caps: \myacro{UNESCO}

\input{template/pdf_settings}  %% should be *last* definitions in preamble!
%% ========================================================================
%%%% begin{document}
%% ========================================================================
\begin{document}

\frontmatter                    %% KOMA: roman page numbers and such; only available in scrbook

\input{colophon}                %% defines information about editor, LaTeX, font, ...

%% Choose your desired title page:
\includepdf{\mytitlepage}            %% include title page

\input{template/declaration_JKU}  %% Statutory Declaration
\input{chapters/acknowledgement}                    
% \input{foreword}              %% this is a suggestion: you have to create this file on demand

%% include the abstract without chapter number but include it on table of contents:
\cleardoublepage
\phantomsection
\addcontentsline{toc}{chapter}{Abstract}
\include{abstract}              %% Abstract

\tableofcontents                %% this produces the table of contents - you might have guessed :-)

\listoffigures

%% if myaddlistoftodos is set to "true", the current list of open todos is added:
\ifthenelse{\boolean{myaddlistoftodos}}{
  \newpage\listoftodos          %% handy if you are using todonotes with \todo{}
}{}                             %% with todonotes-package option "disable" you can get rid of any todo in the output

\mainmatter                     %% KOMA: marks main part using arabic page numbers and such; only available in scrbook

\input{example-short-chapter}   %% remove this line to get rid of the example chapter
\input{example-style-chapter}   %% remove this line to get rid of the style chapter

%% include tex file chapters:
% \include{introduction}        %% this is a suggestion: you have to create this file on demand
% \include{problem}             %% this is a suggestion: you have to create this file on demand
% \include{solution}            %% this is a suggestion: you have to create this file on demand
% \include{evaluation}          %% this is a suggestion: you have to create this file on demand
% \include{outlook}             %% this is a suggestion: you have to create this file on demand

\appendix                       %% closes main document, appendix follows until end; only available in book-classes
\addpart*{Appendix}             %% adding Appendix to tableofcontents

\printbibliography              %% remove, if using BibTeX instead of biblatex
% \include{further_ressources}  %% this is a suggestion: you have to create this file on demand

%%%% end{document}
\end{document}
%% vim:foldmethod=expr
%% vim:fde=getline(v\:lnum)=~'^%%%%\ .\\+'?'>1'\:'='
%%% Local Variables:
%%% mode: latex
%%% mode: auto-fill
%%% mode: flyspell
%%% eval: (ispell-change-dictionary "en_US")
%%% TeX-master: "main"
%%% End:

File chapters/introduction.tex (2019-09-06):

% !TEX root = ../masterthesis.tex
\chapter{Introduction}

In the past century, technology was transformed by the first quantum revolution. Scientists and engineers all around the world utilized certain features of quantum mechanics such as energy quantization and wave-particle duality to create devices which are nowadays a fixed part of everyone's life.
These technologies, ranging from semiconductor devices to LEDs and lasers, became high-performance components which drive modern information processing and global communication networks.
The second quantum revolution to come shall make use of superposition and entanglement~\cite{aharonovich_solid-state_2016}\cite{macfarlane_quantum_2003}.

Entanglement is already the basis of many experiments in quantum computation and its distinct properties can be used for quantum cryptography protocols as well~\cite{zeilinger_light_2017}.
It describes a physical phenomenon involving two or more particles whose quantum states cannot be described independently from each other.
Entanglement is especially useful when the entangled particles are photons, as these can be transported over long distances with optical fibres and are therefore ideal to build up quantum networks~\cite{gisin_quantum_2002}.
Quantum key distribution (QKD) under the E$91$ protocol~\cite{ekert_quantum_1991} can use the quantum network to exchange entangled photons and then generate a shared encryption key.
Since the photons are entangled, the key can be generated in a way which prevents that potential eavesdropping could go unnoticed.
The key is then used to encrypt the data by one party, the encrypted data is transmitted via classical channels and afterwards it is decrypted with the very same key by the other party.
The E$91$ protocol with its use of entanglement has the advantage that it allows to detect eavesdropping even with lossy channels, which is a feature other implementations of QKD cannot necessarily provide.

In order to use entangled photons for QKD several problems have to be solved first.
Fibre and free space channels suffer from decoherence and optical losses~\cite{sangouard_quantum_2011}.
This reduces the amount of photons to a point where their are unsuitable for secure quantum protocols and therefore limits the maximal communication distance.
Usually classical amplifiers would be used to counteract transmission losses, however this does not work with quantum states because of the no cloning theorem~\cite{park_concept_1970}.
In order to solve this problems, multiple teams are currently working on quantum repeaters~\cite{reindl_all-photonic_2018}\cite{duan_long-distance_2001}\cite{simon_quantum_2007}.

The E$91$ protocol and quantum repeaters both require sources of single entangled photons.
Two prominent sources are parametric down conversion crystals~\cite{shih_new_1988} and single atoms~\cite{norden_entangled_2018}\cite{aspect_experimental_1981}.
However the number of entangled photon pairs with parametric down conversion is probabilistic, which means that the number of entangled photon pairs emitted per excitation pulse is statistically distributed.
Single atoms offer sharp electronic transitions, are free from charge fluctuations and are energetically isolated.
Nowadays advanced techniques~\cite{kuhn_deterministic_2002} are used in order to operate with single-atom-based sources, but their arrangements are bulky and their dynamics are relatively low, leading to slow operation rates.

Quantum dots (\acs{QD} \acused{QD}) provide an alternative source of single entangled photons.
\ac{QD} sources are in principle deterministic, with a state preparation probability of approximately \SI{90}{\percent} and a current maximum of \SI{85}{\percent} extraction efficiency~\cite{liu_solid-state_2019}.
Under several conditions, they also emit maximally one photon pair per excitation cycle~\cite{schweickert_-demand_2018}.
With this motivation in mind, droplet-etched GasAs quantum dots as potential sources are investigated in chapter~\ref{chapter:quantum-dot}, as they are quasi strain-free, of high symmetry and exhibit low values of \ac{FSS}.
Optical experiments on \acp{QD} require several methods which are introduced in chapter~\ref{cha:methods}. 
Usually, entangled photon pairs are obtained by exciting the biexciton state via resonant two-photon excitation.
However, resonant two-photon excitation typically requires precise control of the intensity of the exciting field in order to invert the quantum dot from the ground state to the biexciton state~\cite{jayakumar_deterministic_2013}.
Adiabatic rapid passage and alternative excitation schemes using frequency-chirped pulses do not suffer from this requirement, which motivates their discussion in chapter~\ref{cha:chirp}.

Quantum repeaters rely on indistinguishable photons, which means that they match in all possible parameters and degrees of freedom.
Indistinguishability could be estimated by analysing the time-averaged line shape~\cite{reindl_all-photonic_2018}. However, fine features of the emission spectrum are not resolvable with a standard CCD-based spectrometer alone.
A \ac{FPI} can be used to resolve \ac{QD} emission spectra while still using the same spectrometer as an accurate power meter.
A \ac{FPI} transmits signals of certain frequencies and these frequencies can be adjusted in order to scan through the ranges of interest.
\ac{QD} emission is sent through the scanning interferometer and its output power is then recorded with the CCD allowing to reassemble the complete spectrum.
Chapter~\ref{chapter:scanning-fabry-perot} describes the efforts to build up a scanning \ac{FPI} to do exactly that.
Chapter~\ref{cha:summary} summarises the work discussed in this thesis and gives a brief outlook to the next steps.

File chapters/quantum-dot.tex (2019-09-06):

% !TEX root = ../masterthesis.tex
\chapter{Gallium arsenide quantum dots}
\label{chapter:quantum-dot}

\section{Fabrication and optical properties}

Quantum dots (\acs{QD}) are nanostructures which confine the motion of electrons and holes in all three spatial dimensions.
Confinement results in discrete energy levels, which is why \acp{QD} are sometimes referred to as \textit{artificial atoms}.
The discussion in this section is based on the PhD thesis of \textcite{huber_gaas_2019} and on the master's thesis of \textcite{schimpf_towards_2017}.

The Gallium arsenide \acp{QD} investigated within this master's thesis are grown by \ac{MBE} with the self-assembled nanodrill technology described in the work of \textcite{wang_nanoholes_2007}.
As displayed in figure~\ref{fig:droplet-etched-gaas-qds}a the Al forms droplets on Al$_{0.4}$Ga$_{0.6}$As after evaporation.
The Al reacts with Al$_{0.4}$Ga$_{0.6}$As, etching nanoholes into the surface.
Under ideal conditions, these nanoholes are highly symmetric, resulting into \acp{QD} with high in-plane symmetry, as can be seen in figure~\ref{fig:droplet-etched-gaas-qds}b.
The next step is the annealing process, in which GaAs is deposited to fill the nanoholes.
The \ac{QD} is finalized by capping the layer with Al$_{0.4}$Ga$_{0.6}$As acting as top barrier.

Compared to the band gap of the host material Al$_{0.4}$Ga$_{0.6}$As of \SI{1.92}{\electronvolt} at room temperature, the core of the \ac{QD}, GaAs has a band gap of only \SI{1.42}{\electronvolt} at room temperature.
The energy difference between the bandgaps and the type-I band alignment depicted in figure~\ref{fig:droplet-etched-gaas-qds}c are responsible for the 3D confinement, leading to discrete energy levels.
Inside of the \ac{QD}, optical transitions are possible.
Transitions between the first energy level in the \ac{CB} and the \ac{VB}, often called the s-shell, are here of special interest.
The carriers involved are the electrons ($e^-$) and the holes ($h^+$) left behind.
These are fermions and therefore only up to two of them can, in accordance with Pauli's exclusion principle, occupy a single energy state.
Electrons and holes are strongly localized inside the \ac{QD} by the confinment potential and influence each other by Coulomb attraction and exchange interaction~\cite{bimberg_quantum_1999}.
This leads to multi-particle complexes with the most fundamental being the \acf{X}, a quasi-particle consisting of an electron and a hole, bound by Coulomb interaction.
Fully occupied s-shells form the \acf{XX}, consisting of two electrons and two holes of opposite spins.

\begin{figure}[H]
	\centering
	
	\caption[Droplet etched GaAs quantum dots.]{(a) The growth process of a GaAs quantum dot by \ac{MBE}.\\
	(b) Atomic force microscopy (AFM) image of the nanohole before it is filled with GaAs.\\
    (c) Conduction band (CB) and valence band (VB) of an optically active QD.~\cite{huber_gaas_2019}}
	\label{fig:droplet-etched-gaas-qds}
\end{figure}
In a \ac{QD}, polarization-entangled photon pairs can be generated via a biexciton-exciton decay cascade~\cite{stevenson_semiconductor_2006}, illustrated in figure~\ref{fig:biexciton-exciton-cascade}.
The $\ket{XX}$ state forms a full shell, which means that the total angular momentum projection along the quantization axis of the \ac{XX} complex sums up to $M=0$.
If the \ac{QD} is radially symmetric, $M$ is preserved and $\ket{M}$ are eigenstates of the system.
After exciting the \ac{QD} into the $\ket{XX}$ state (e.g. by optical pumping) it decays by spontaneous recombination of an electron-hole-pair accompanied by the emission of a single photon into the $\ket{X}$ state.
\newpage
The two dipole-allowed radiative transitions lead to only two possible angular momentum states of the exciton:
\begin{itemize}
	\item $\ket{-1}$ under emission of a right-circularly-polarized photon $\ket{R_{XX}}$
	\item $\ket{+1}$ under emission of a left-circularly-polarized photon $\ket{L_{XX}}$
\end{itemize}
$\ket{-1}$ and $\ket{+1}$ are degenerated in energy and decay into the groundstate $\ket{G}$ under emission of $\ket{L_X}$ and $\ket{R_X}$, respectively.
The resulting two-photon state is then described by
\begin{equation}
\ket{\psi^+}=\frac{1}{\sqrt{2}}\left(\ket{L_{XX}}\ket{R_X}+\ket{R_{XX}\ket{L_X}}\right)
\end{equation}
which is one of the four Bell states, representing the maximally entangled two-particle states.

\begin{figure}[H]
	\centering
	
	\caption[Biexciton-exciton decay cascade in a QD.]{Biexciton-exciton decay cascade in a QD.
			The $\ket{XX}$ state can decay via two paths under the emission of a right (left) polarized photon into one of two energetically degenerated $\ket{X}$ states.
			The $\ket{X}$ state then decays into the ground state $\ket{G}$ under the emission of a left (right) polarized photon.~\cite{huber_gaas_2019}}
	\label{fig:biexciton-exciton-cascade}
\end{figure}

In order to calculate the life time of the \ac{X} and \ac{XX} states and the respective spectral distribution of the emission, the radiative transition rate $\Gamma$ between quantum mechanical states has to be derived.
$\Gamma$ describes the transition probability per unit time from an initial state $\ket{i}$ to a final state $\ket{f}$ and can be calculated by Fermi's golden rule if the the transition occurs because of a weak perturbation.
In the dipole approximation it depends on
\begin{equation}
\Gamma \propto \left|\braket{f|\mathbf{e}\cdot\mathbf{\hat{p}}|i}\right|^2 \delta(E_i-E_f-E_P)
\end{equation}
with $\mathbf{e}$ the unit polarisation vector of the emission, $\mathbf{\hat{p}}$ the momentum operator of the electron and $E_f$, $E_i$ and $E_P$ the energies of the final state, of the initial state and of the emitted photon respectively.
The rate equation for the population of the initial state can then be expressed as
\begin{equation}
\frac{dN_i(t)}{dt} = - \Gamma N_i(t)
\end{equation}
which results into exponential decay as solution
\begin{equation}
N_i(t) = N_i(0)e^{-t/\tau}
\end{equation}
where the lifetime of the initial state is defined as $\tau = 1/\Gamma$.

This can be applied for the \ac{X} and \ac{XX} states with decay constants $\tau_\nu$ and intensity for the emitted light $I_\nu(t)$, where $\nu \in \{X,XX\}$.
The Fourier transform of the electric field yields a Cauchy distribution
\begin{equation}
I_{\nu}(\omega) = \frac{1}{2\pi\tau_\nu}\frac{1}{(\omega-\omega_\nu)^2+\left(\frac{1}{2\tau_\nu}\right)^2}
\end{equation}
with $\omega_\nu=e_\nu/\hbar$ denoting its center frequency.

\section{Fine structure splitting}

The \ac{FSS} in a \ac{QD} describes the energy splitting between the two possible bright $\ket{X}$ states, which originates from the exchange interaction between electrons and holes.~\cite{bayer_fine_2002}.
The electron-hole exchange Hamilton is described by
\begin{equation}
\label{eq:hamiltonian}
\mathcal{H}_{ex} = - \sum_{i=x,y,z}a_i J_{h,i}S_{e_i}+b_i J^3_{h_i}S_{e_i}
\end{equation}
with $a_i$ and $b_i$ the spin-coupling constants, $J_{h_i}$ the holes' and $S_{e_i}$ the electrons' total angular momentum.
The $z$-direction is assigned as the crystal growth direction and the bright \ac{X} states are defined by the projections of $J_{\textbf{h}}$ and  $S_{\textbf{e}}$ to the $z$-axis, so that $\ket{+1} =\ket{+\frac{3}{2},-\frac{1}{2}}$ and $\ket{-1}=\ket{-\frac{3}{2},+\frac{1}{2}}$.
The Hamiltonian of equation~\eqref{eq:hamiltonian} can then be described in the bases $\{\ket{+1},\ket{-1}\}$
\begin{equation}
\mathcal{H}_{ex}=
\begin{pmatrix}
\braket{+1|\mathcal{H}_{ex}|+1} & \braket{+1|\mathcal{H}_{ex}|-1} \\
\braket{-1|\mathcal{H}_{ex}|+1} & \braket{-1|\mathcal{H}_{ex}|-1}
\end{pmatrix}
=
\begin{pmatrix}
\Delta_0 & \Delta_1 \\
\Delta_1 & \Delta_0
\end{pmatrix}
\end{equation}
with $\Delta_0=\frac{3}{4}(a_z+\frac{9}{4}b_z)$ and $\Delta_1=-\frac{3}{8}(b_x-b_y)$.

In the ideal case in which the \ac{QD} is perfectly symmetric along the $z$-axis, $b_x=b_y$, $\Delta_1$ vanishes and $\ket{+1}$ and $\ket{-1}$ are degenerate eigenstates.
If that is not the case, the angular momentum $M$ along the $z$-direction is not preserved and $\ket{+1}$ and $\ket{-1}$ are no eigenstates of $\mathcal{H}_{ex}$.
The new basis can be found by diagonalising $\mathcal{H}_{ex}$ and is described by $\frac{1}{\sqrt{2}}(\ket{+1}+\ket{-1})$ and $\frac{1}{\sqrt{2}}(\ket{+1}-\ket{-1})$.
In figure~\ref{fig:qd-energy-levels-fss} the $\ket{XX}$ decay path with splitted $\ket{X}$ eigenstates is shown.  $\ket{XX}$ exhibit no splitting as the angular momentum of the electrons and holes add to zero and therefore no exchange interaction occurs.
In figure~\ref{fig:fss-pol} photo-luminescence spectra recorded with a linear polariser are shown.
\begin{figure}[H]
	\centering
	\begin{subfigure}[b]{0.48\textwidth}
		\centering
		
		\caption{XX decay cascade without X degeneracy because of fine structure splitting.~\cite{huber_gaas_2019}\\}
		\label{fig:qd-energy-levels-fss}
	\end{subfigure}%
	~ % An dieser Stelle kann ein zusätzlicher Zwischenraum eingebunden werden: ~, \quad, \qquad, \hfill usw.
	% Eine leere Zeile erzwingt, dass die zweite Grafik darunter erscheint.
	\begin{subfigure}[b]{0.48\textwidth}
		\centering
		
		\caption{Photoluminescence spectra of X emission of a GaAs QD plotted for different polarizer angles.
			In the image the effect of the linear polarization of the fine structure components is visible.~\cite{schimpf_towards_2017}}
		\label{fig:fss-pol}
	\end{subfigure}
	\caption{Fine structure splitting in a GaAs quantum dot.}
	\label{fig:fss}
\end{figure}

\newpage
\section{Zero-phonon line and phonon sideband}
\label{sec:zero-phonon-side-band}
The excitonic emission of GaAs \acp{QD} (and of solid-state quantum emitters in general) exhibits non-Lorentzian asymmetric broadening.
These side bands can be traced back to a coupling to acoustic phonons \cite{peter_phonon_2004}\cite{reigue_probing_2017}.
The discussion of \acp{PSB} is based on the works of \textcite{friedrich_photochemical_1984} and  \textcite{peter_phonon_2004}.

Figure~\ref{fig:line-shape} displays a schematic representation of the \ac{ZPL} and \ac{PSB} absorption spectrum.
The intensity distribution between the two components depends strongly on temperature and can be described by the \ac{FCP}~\cite{franck_elementary_1926}.
\begin{figure}[H]
	\centering
	
	\caption[Absorption line shape of an electronic excitation.]{Absorption line shape of an electronic excitation.
		The emission shape can be determined by mirroring the absorption shape at $\omega'$.}
	\label{fig:line-shape}
\end{figure}
The \ac{FCP} state that electronic transition between ground and excited state is much faster than the motion in the lattice, which is why there is no motion along the configurational coordinates $q_i$ during the energy transitions as depicted in figure~\ref{fig:phonon-energy-diagram}.
The transitions can be displayed as vertical arrows with the shorter arrow describing the \ac{ZPL} and the longer one describing the \ac{PSB}.
According to the \ac{FCP}, the more the wave functions of two vibrational energy levels overlap, the likelier is the electronic transition between these two.
In the case of figure~\ref{fig:phonon-energy-diagram} this occurs when the photon energy equals to the energy difference $E_1-E_0$ plus three quanta of vibrational energy $E_{pi} = \hbar \Omega_i$.
The emission follows the same principle.
\begin{figure}[H]
	\centering
	\begin{subfigure}[b]{0.48\textwidth}
		\centering
		
		\caption{Energy spectrum of a two-level electronic system with phonon coupling.
			The arrows describe emission/absorption with and without phonons respectively.}
		\label{fig:phonon-energy-diagram}
	\end{subfigure}%
	~ % An dieser Stelle kann ein zusätzlicher Zwischenraum eingebunden werden: ~, \quad, \qquad, \hfill usw.
	% Eine leere Zeile erzwingt, dass die zweite Grafik darunter erscheint.
	\begin{subfigure}[b]{0.48\textwidth}
		\centering
		
		\caption{Three lattice normal modes $(i, j, k)$ and the resulting emission/absorption spectrum.\\}
		\label{fig:lattice-modes}
	\end{subfigure}
	\caption{Zero-phonon line and phonon sideband.~\cite{noauthor_zero-phonon_nodate}}
	\label{fig:zero-phonon-line-phonon-side-band}
\end{figure}

Figure~\ref{fig:phonon-energy-diagram} and \ref{fig:lattice-modes} implicitly assume approximations in addition to the \ac{FCP}.
The lattice vibrational mode has to be well described by a quantum harmonic oscillator.
Additionally, it is assumed that only the lowest lattice vibration is excited and that the harmonic oscillator potentials are equal in both states.
These preconditions are visible in the parabolic shaped potential wells and equally spaced phonon energy levels in figure~\ref{fig:phonon-energy-diagram}.

Each lattice mode $m$ leads to a different energy difference $\hbar \Omega_m$ between phonons.
That is why the transitions with phonons result in a energy distribution and the zero-phonon transition add up at the electronic origin $E_1 - E_0$ as can be seen in figure~\ref{fig:lattice-modes}.

\newpage

The theoretical limit of the spectral range of the zero-phonon line for a GaAs quantum dot can be calculated with the time-energy uncertainty relation
\begin{equation}
\Delta E \cdot \Delta t = \frac{h}{2 \pi}
\end{equation}
This gives for a typical lifetime of a GaAs quantum dot of $\Delta t = \SI{250}{\pico \second}$
\begin{equation}
\Delta E = \SI{2.64}{\micro \electronvolt}.
\end{equation}
The frequency uncertainty can be obtained through
\begin{equation}
\label{eq:planck-einstein}
\Delta \nu = \frac{\Delta E}{h}.
\end{equation}
The wavelength $\lambda$ relates to $\nu$ with the Planck-Einstein relation
\begin{equation}
\lambda(\nu) = \frac{c}{\nu}
\end{equation}
and the wavelength uncertainty $\Delta \lambda$ can be approximated with a Taylor series around $\nu_0$
\begin{align}
\Delta \lambda = - \lambda'(\nu_0)\cdot \Delta \nu.
\end{align}
With equation~\eqref{eq:planck-einstein} and the center wavelength of the zero-phonon line $\lambda_{0}$ in table~\ref{tab:quantum-dot-emission} this gives
\begin{align}
\Delta \lambda &= \frac{c}{\nu_0^2} \cdot \Delta \nu = \frac{\lambda_0^2}{c}\cdot\Delta \nu\\
\label{eq:zero-phonon-theoretical-limit}
&\approx \SI{1.0}{\pico \metre}
\end{align}

In practise, the \ac{ZPL} is broadened by pure-dephasing due to interaction with phonons. 
Together with data from \textcite{scholl_resonance_2019} and empirical values measured by our group, this leads to the parameters listed in table~\ref{tab:quantum-dot-emission}.

\begin{table}[H]
	\caption[Paramters of GaAs quantum dots used in the laboratory of semiconductor physics department in Linz.]{Parameters of GaAs quantum dots used in the laboratory of semiconductor physics department in Linz.
		Zero-phonon line calculates from the theoretical limit according to the lifetime of the excitonic state (as can be seen in equation~\eqref{eq:zero-phonon-theoretical-limit}).
		The phonon sideband resembles data taken from \textcite{scholl_resonance_2019}.}
	\label{tab:quantum-dot-emission}
	\begin{tabular}{@{}llll@{}}
		\toprule
		Quantum dot emission & Center wavelength $\lambda_0$           & Spectral range $\Delta \lambda$ & Waveform                  \\ \midrule
		Zero-phonon line               & \SIrange{700}{800}{\nano \metre} & \SIrange{1.0}{1.4}{\pico \metre} & Cauchy\\
		Phonon sideband       & \SI{\sim 0.25}{\nano \metre} higher than zero-phonon line  & ~\SI{500}{\pico \metre} & Gauss  \\ \bottomrule
	\end{tabular}
\end{table}

\newpage

\section{Optical excitation of a quantum dot}
In this section, different ways of optically exciting \acp{QD} are discussed.
It is based on the PhD thesis of \textcite{huber_gaas_2019} and the master's thesis of \textcite{schimpf_towards_2017}.
The excited states of a \ac{QD} can be populated in various ways.
A common way is above-band excitation, depicted in figure~\ref{fig:optical-pumping-quantum-dot}a.
Electrons are optically excited by a laser with energies above the band gap of the \acp{QD} host material Al$_{0.4}$Ga$_{0.6}$As with $E_L = \SI{1.92}{\electronvolt}$ at room temperature.
Subsequently, electrons and holes are captured by the \acp{QD} and relax via phonon-scattering to the lowest energy level, the s-shell.
However, because of pronounced recapture processes~\cite{kuroda_symmetric_2013} and spin scattering processes~\cite{michler_single_2009}, above-band excitation is not favourable for entangled photon generation.
Additionally, indistinguishability of the emitted photons is reduced because of fluctuating electric fields and time-jitter induced by the relaxation process.
Resonant excitation of electron-hole pairs provides an alternative to alleviate these effects.
As shown in figure~\ref{fig:optical-pumping-quantum-dot}b this technique creates electron-hole-pairs directly in the s-shell.
\begin{figure}[H]
	\centering
	
	\caption{Optical pumping of a QD by	(a) above-band excitation and (b) resonant excitation~\cite{huber_gaas_2019}}
	\label{fig:optical-pumping-quantum-dot}
\end{figure}
Resonant excitation can be used in order to populate the $\ket{XX}$ state with near unity population probability~\cite{reindl_phonon-assisted_2017}.
Due to dipole-selection rules, this requires a two-photon-absorption process.
Hereby, the energy of a femtosecond-pulse laser $E_p$ is tuned to exactly the half of the \ac{XX} energy with respect to the ground energy, as sketched in figure~\ref{fig:qd-resonant}.
Because of Coulomb interaction, two times the \ac{X} energy with respect to the ground energy $2 \cdot E_X$ is not equal to $E_{XX}$ but differs by the binding energy $E_B$.
The laser is therefore tuned to
\begin{equation}
\label{eq:e_p}
E_P = E_X - E_B / 2
\end{equation}
with $E_B \approx \SI{3.78}{\milli \electronvolt}$ for GaAs \acp{QD}.
Resonant two-photon absorption is a third-order non-linear effect which involves two photons and electrons at once.
It depends on the third-order-susceptibility $\chi^{(3)}$ of GaAs and therefore requires relatively high laser power.

As this two-level system is driven in resonance, its population exhibits Rabi oscillations.
The final population of the \ac{XX} can be described by
\begin{equation}
\label{eq:n-xx}
N_{XX} = \sin^2\left(\frac{\theta}{2}\right)
\end{equation}
with $\theta$ as the pulse area in relation to the Rabi oscillations.
It has to be noted that $\theta$ is not the area of the excitation pulse, but depends on it in a non-trivial way~\cite{stufler_two-photon_2006}.
Measured Rabi oscillations of \ac{X} and \ac{XX} are shown in figure~\ref{fig:rabi-oscillations}~\cite{reindl_phonon-assisted_2017}.
Theoretically, the curve should oscillate between occupancies $N/N_0$, with $N_0$ as the maximum population, of $0$ and $1$.
However, as a consequence of phonon damping the occupancy converges to a purely probabilistic value of $0.5$~\cite{forstner_phonon-assisted_2003}.
\begin{figure}[H]
	\centering
	\begin{subfigure}[b]{0.48\textwidth}
		\centering
		
		\caption{Resonant two photon excitation of \ac{XX}.\\
			The laser is tuned to $E_P = E_{XX} / 2$.}
		\label{fig:qd-resonant}
	\end{subfigure}%
	~ % An dieser Stelle kann ein zusätzlicher Zwischenraum eingebunden werden: ~, \quad, \qquad, \hfill usw.
	% Eine leere Zeile erzwingt, dass die zweite Grafik darunter erscheint.
	\begin{subfigure}[b]{0.48\textwidth}
		\centering
		
		\caption{Rabi oscillations of \ac{X} and \ac{XX} as a function of the pulse area $\theta$.
				$N/N_0$ is the occupancy and $N_0$ the maximum population.}
		\label{fig:rabi-oscillations}
	\end{subfigure}
	\caption{Resonant two photon excitation~\cite{schimpf_towards_2017}}
	\label{fig:resonant-two-photon-excitation}
\end{figure}
\section{Single photon emission}
The \ac{XX}-\ac{X} decay cascade shown in figure~\ref{fig:qd-resonant} results in a single photon pair per emission cycle.
Single photons are necessary for quantum cryptography and quantum optics in general, which motivates the following discussion of this topic based on the thesis of \textcite{huber_gaas_2019}.
The single photon purity of the $\ket{XX}$ to $\ket{X}$ and the $\ket{X}$ to $\ket{G}$ decay emissions, respectively, can be determined by performing a \acf{HBT} experiment.
An example of an \ac{HBT} setup is shown in figure~\ref{fig:hbt-fiber} and consists of two \acp{APD} used as single photon detectors and a beam splitter.
The measurements at the two detectors can be used in order to calculate the second-order correlation function
\begin{equation}
g^{(2)}(\tau) = \frac{\langle n_1(t) n_2(t+\tau)\rangle}{\langle n_1(t) \rangle \langle n_2(t+\tau) \rangle}
\end{equation}
where $n_i(t)$ is the number of counts registered on \ac{APD} $i$ at time $t$ and $\tau$ is the time delay. When a single photon enters the input of the \ac{BS}, it can only be measured at one output, but never at both simultaneously.
Assuming a perfect single photon emitter, a coincidence measurement between \ac{APD}~$1$ and \ac{APD}~$2$ will result in $g^{(2)}(\tau=0) = 0$.
Subsequently, side peaks are expected at $\tau_s=z/R$ with $R$ as the repetition rate of the laser and $z\in \mathbb{Z}\backslash \{0\}$.
The single photon purity can then be defined as
\begin{equation}
\kappa(b) = \frac{A_0(b)}{A_s(b)}
\end{equation}
with $A_0$ as the area under $g^{(2)}(\tau)$ around $\tau=0$ and $A_s$ as the average area under the side peaks at $\tau_s$.
The time bin $b$ has to be chosen so that it includes a full side peak.
If $b$ would be chosen too small it would falsely increase $\kappa$, if chosen too high it would include unnecessary much noise.

\begin{figure}[H]
	\centering
	\begin{subfigure}[b]{0.48\textwidth}
		\centering
		
		\caption{Setup to measure the Hanbury-Brown-Twiss effect.
		Single photons can be measured only at one APDs, but not at both at the same time.}
		\label{fig:hbt-fiber}
	\end{subfigure}%
	~ % An dieser Stelle kann ein zusätzlicher Zwischenraum eingebunden werden: ~, \quad, \qquad, \hfill usw.
	% Eine leere Zeile erzwingt, dass die zweite Grafik darunter erscheint.
	\begin{subfigure}[b]{0.48\textwidth}
		\centering
		
		\caption{Second-order auto-correlation function $g^{(2)}$ of \ac{X} and \ac{XX}.
		The low height of the peak at zero time delay compared to the height of the side peaks suggest the suitability of the quantum dot as a single photon emitter.}
		\label{fig:gs2-x-xx}
	\end{subfigure}
	\caption{Hanbury-Brown-Twiss \acs{HBT} experiment~\cite{schimpf_towards_2017}}
	\label{fig:hbt}
\end{figure}

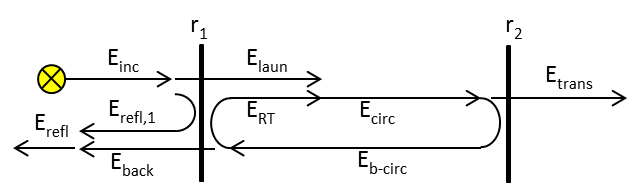
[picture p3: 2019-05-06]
figures/fabry-perot/Schematic_of_the_Fabry-Perot_interferometer.png

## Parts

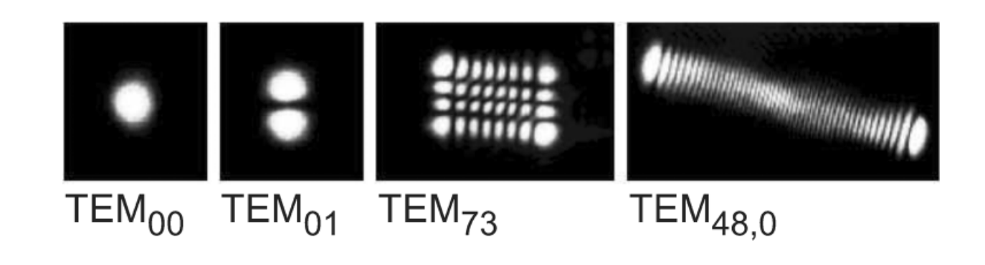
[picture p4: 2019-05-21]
figures/fabry-perot/gauss-modes-higher-order.PNG

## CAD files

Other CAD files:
figures/setup/processing/Setup_flat.dwg

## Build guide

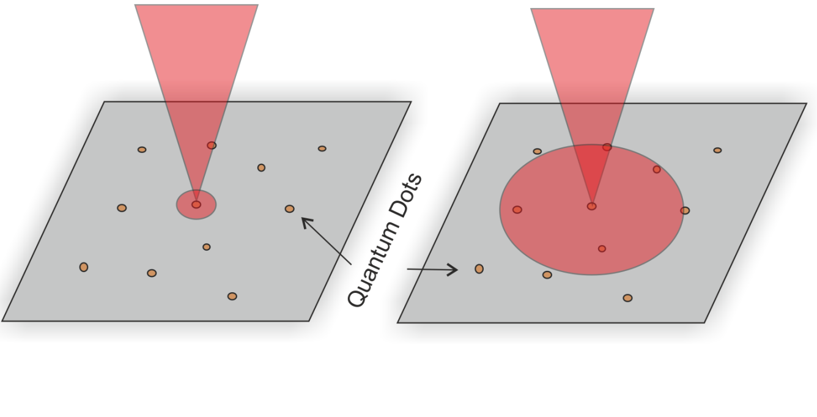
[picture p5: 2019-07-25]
figures/setup/micro-pl.png

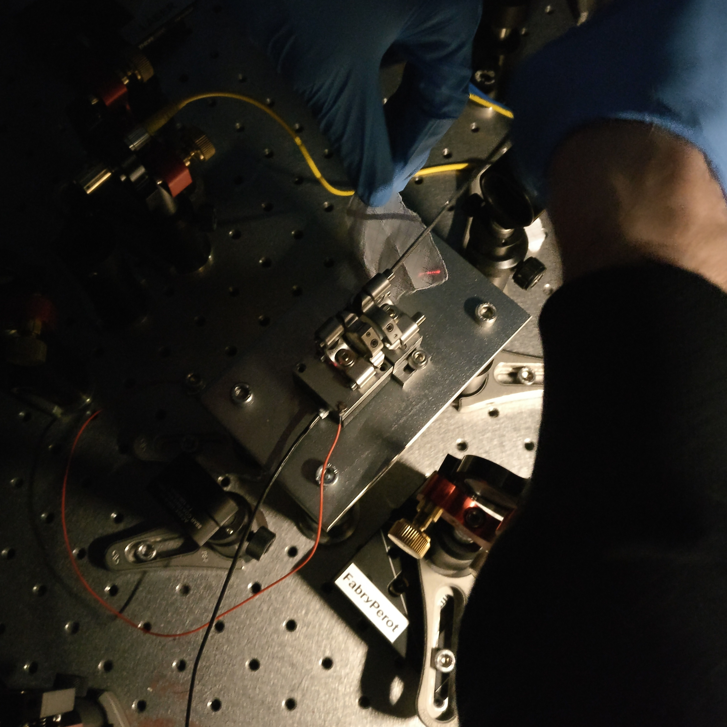
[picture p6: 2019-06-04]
figures/fabry-perot/setup/setup-higher-modes-2.jpg

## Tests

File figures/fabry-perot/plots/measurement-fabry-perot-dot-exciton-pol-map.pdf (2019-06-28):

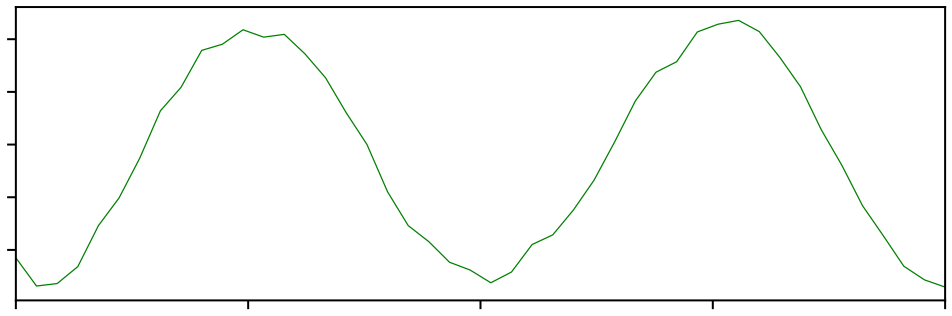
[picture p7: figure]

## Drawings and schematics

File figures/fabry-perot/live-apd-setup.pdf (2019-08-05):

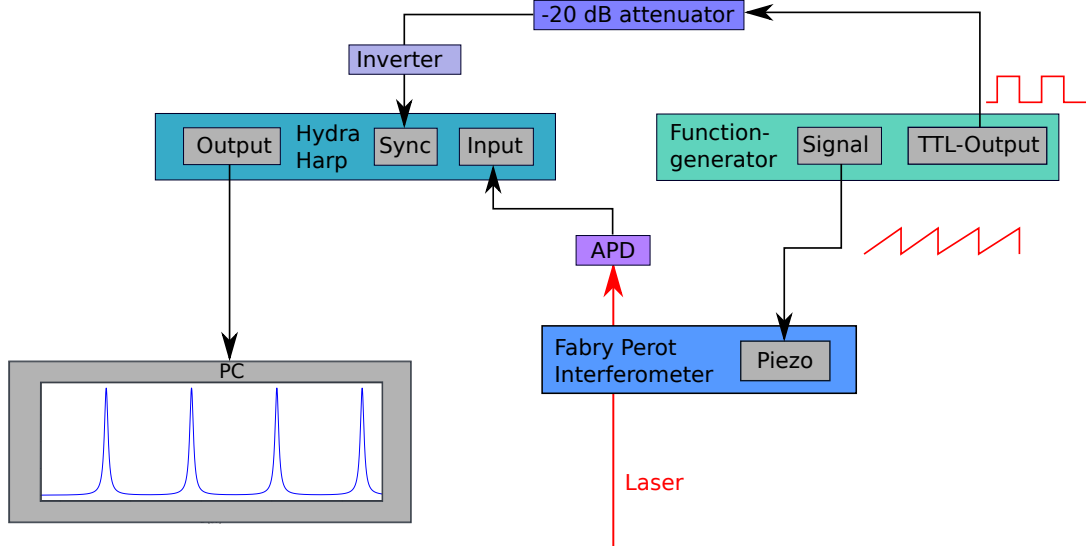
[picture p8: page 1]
Fabry Perot; Interferometer; Piezo; -20 dB attenuator; APD; Hydra; Harp; Sync; Input; Function-; generator Signal; TTL-Output; Output; Laser; Inverter

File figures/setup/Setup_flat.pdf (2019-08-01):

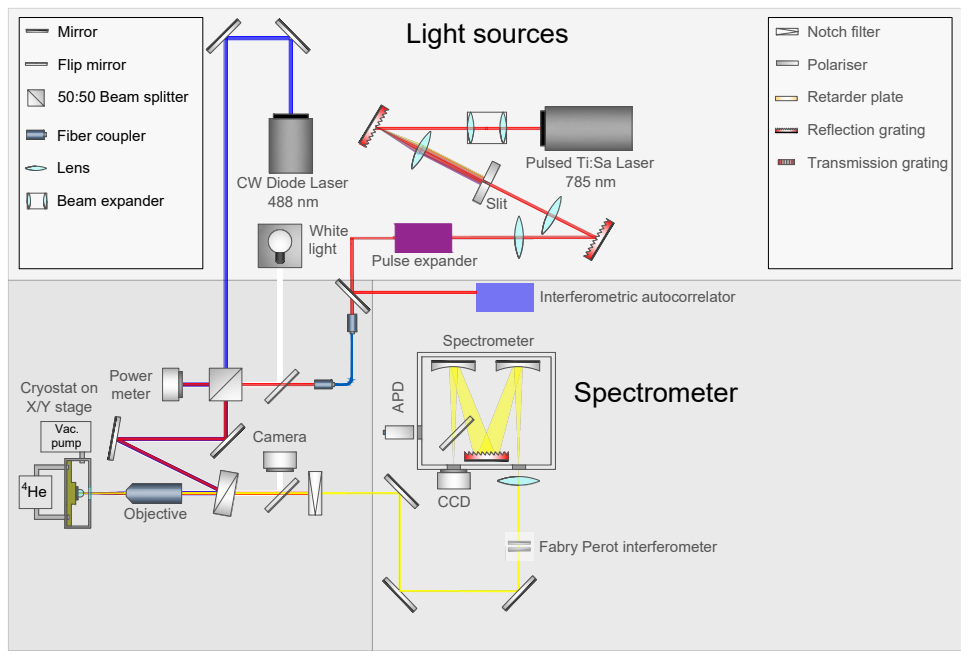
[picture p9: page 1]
Camera Objective; Spectrometer CCD; Spectrometer Light sources Slit CW Diode Laser 488 nm; Pulsed Ti:Sa Laser 785 nm Power meter Mirror Flip mirror 50:50 Beam splitter Fiber coupler Lens Beam expander; Notch filter Polariser Retarder plate Reflection grating Transmission grating Vac. pump; White light 4He Cryostat on X/Y stage

APD Fabry Perot interferometer Interferometric autocorrelator Pulse expander

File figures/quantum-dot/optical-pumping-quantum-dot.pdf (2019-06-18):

a
b

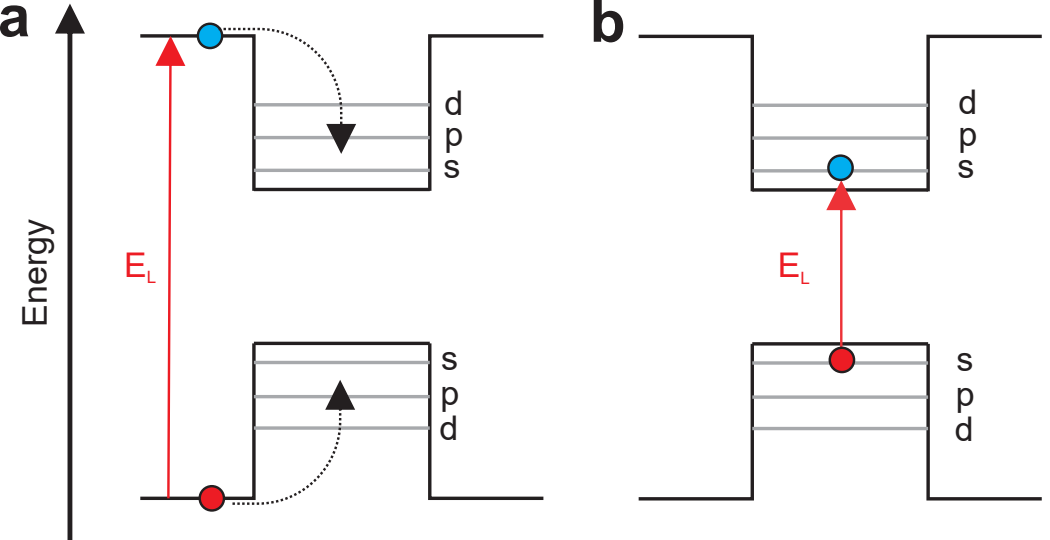
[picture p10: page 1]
Energy; spdspd

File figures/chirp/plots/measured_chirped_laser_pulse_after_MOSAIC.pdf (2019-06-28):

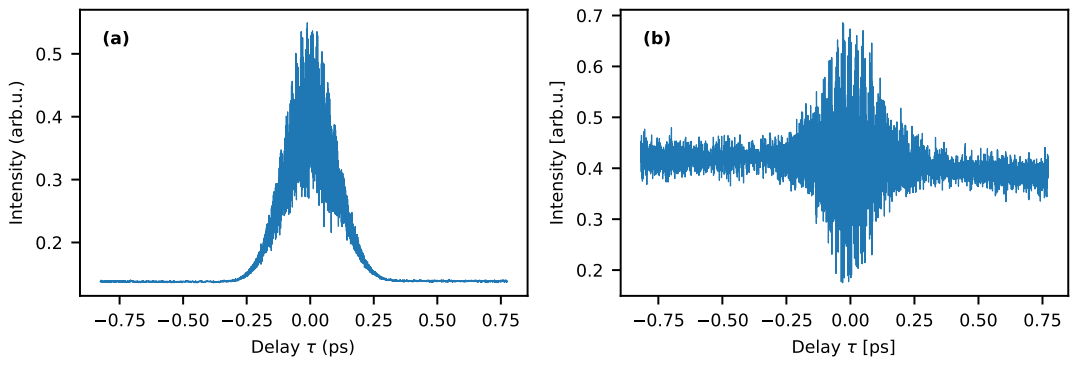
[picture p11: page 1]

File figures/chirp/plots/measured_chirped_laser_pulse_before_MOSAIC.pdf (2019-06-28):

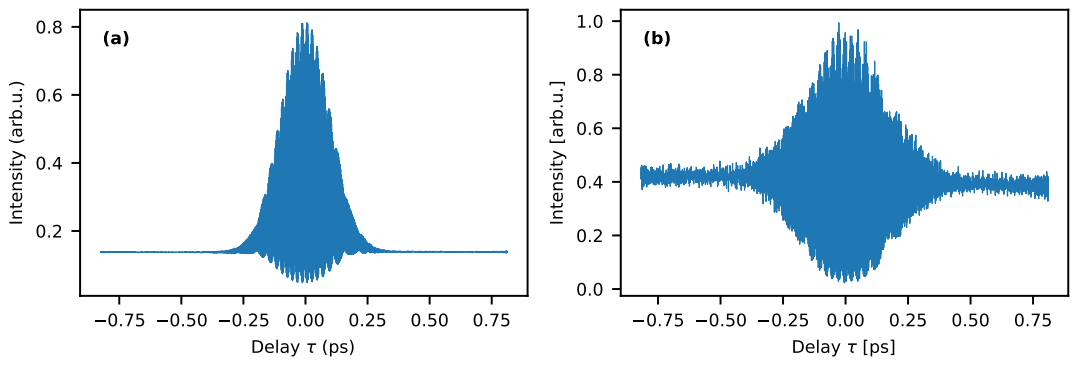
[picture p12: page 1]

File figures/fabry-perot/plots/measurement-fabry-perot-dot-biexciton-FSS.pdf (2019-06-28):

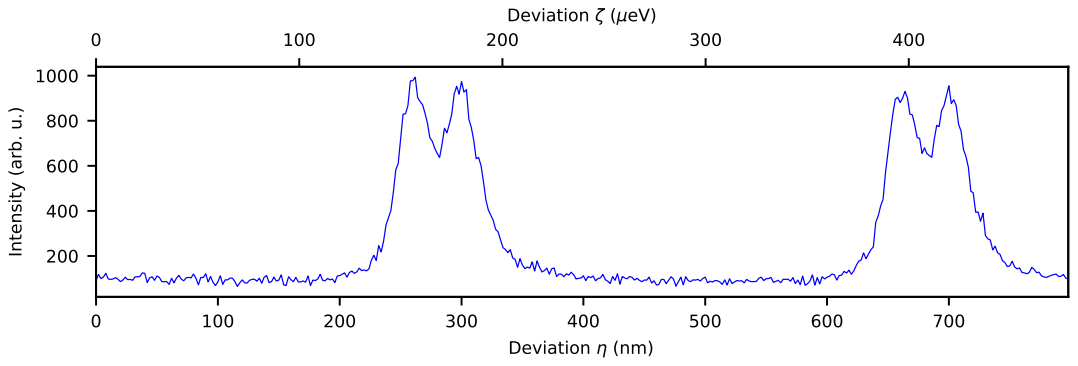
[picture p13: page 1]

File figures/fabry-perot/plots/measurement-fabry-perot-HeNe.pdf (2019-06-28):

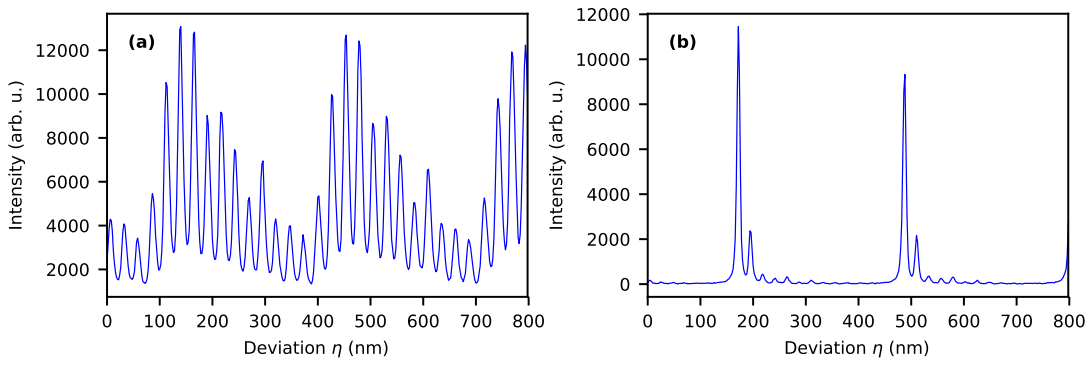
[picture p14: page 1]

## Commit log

2019-06-25 Chirp: IAC and simulation + a little bit FPI
    [Setup_flat.dwg]
2019-06-27 Fabry Perot: APD live setup and a lot of plots
    [Setup_flat.dwg]
2019-07-01 Introduction and FPI Simulations
    [Setup_flat.dwg]
2019-07-11 Adjustments to setup and figure captions
    [Setup_flat.dwg]
2019-07-11 Save autocad files
    [Setup_flat.dwg]
2019-07-29 Continue to implement Christians suggestions
    [Setup_flat.dwg]
